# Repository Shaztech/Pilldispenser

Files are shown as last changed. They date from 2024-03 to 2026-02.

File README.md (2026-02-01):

# Automatic Pill Dispenser

Complete open source project with cheap and easily available parts (listing below).
All 3d printable parts are in STL format (go to makerworld for the 3D Models), Gerber PCB are packed in zip for easy drag-drop in 
your prefered provider (JCLPCB, PCBWay, etc).
Software are available in pre-compiled (bin files) for the ESP32, or all Arduino files are there so you can 
edit them. I've included all the library I used. The full LCD interface is in Squareline Studio.
Just follow the guides in order to assemble it once you have all the parts.

Please check the user manual for the usage of the device.

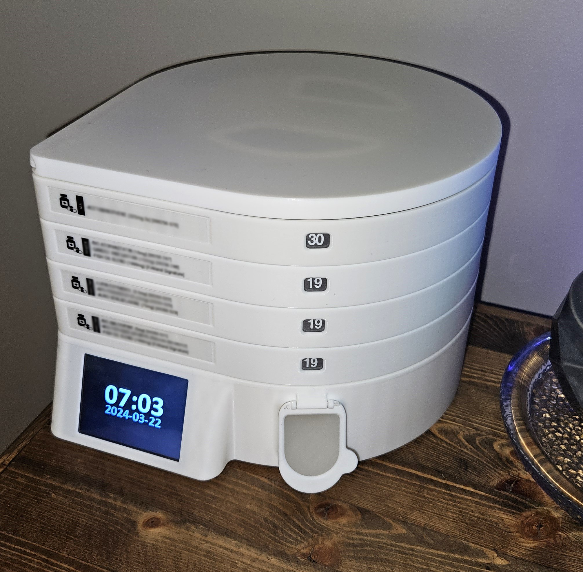
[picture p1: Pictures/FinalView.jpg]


## Features:
- USB Powered (5V, 500mah)
- Wifi configuration directly on the screen
- NPT automaticaly updated time (Need Wifi for the time to work)
- UTC/DST configurable on the screen
- Time/Date screensaver (can be disabled)
- Full interface on the touch screen
- Multiples users can be defined by colors
- Audio/Visual Alarms for each tray/users (audio alarms are repeated every minute till dispensed)
- Alarms are mp3 files on the SD card (so can be changed by the user)
- Can stack up to 10 trays
- 30 sections (can accomodate multiple/large pills) for each tray
- Manual dispense of each tray
- Visual indication of remaining pills (P-Touch label 30 to E)
- Web interface for easy configuration with browser
- Telegram integration
- [Home Assistant Integration](https://github.com/demrios-de/Pill-Dispenser-Integration-for-Home-Assistant) [EN/DE] (made by [demrios](https://github.com/demrios-de))

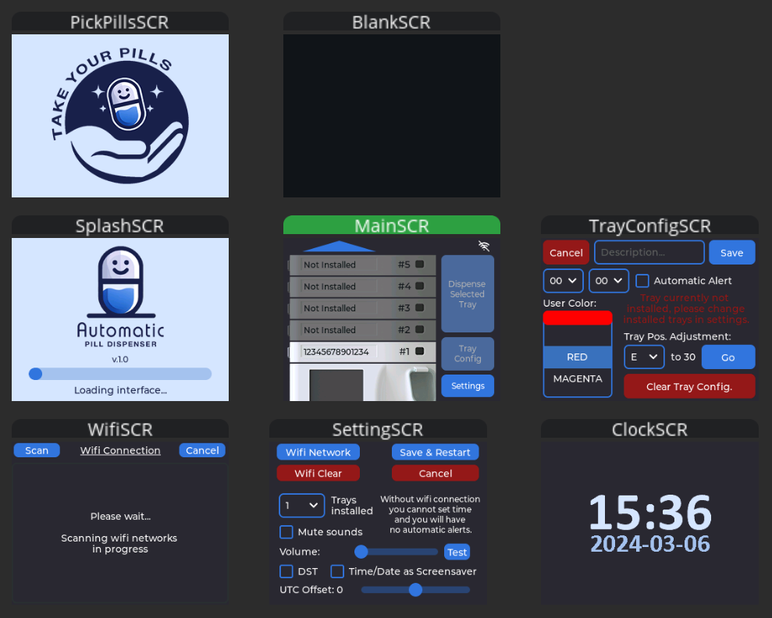
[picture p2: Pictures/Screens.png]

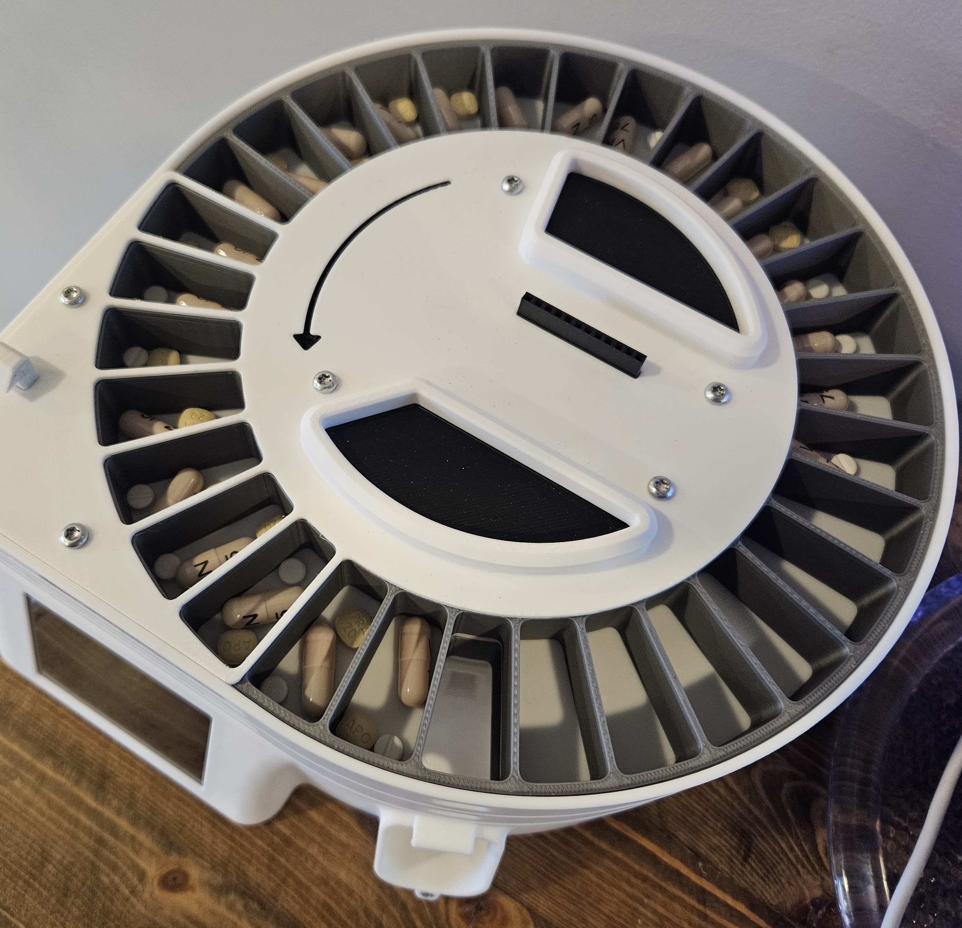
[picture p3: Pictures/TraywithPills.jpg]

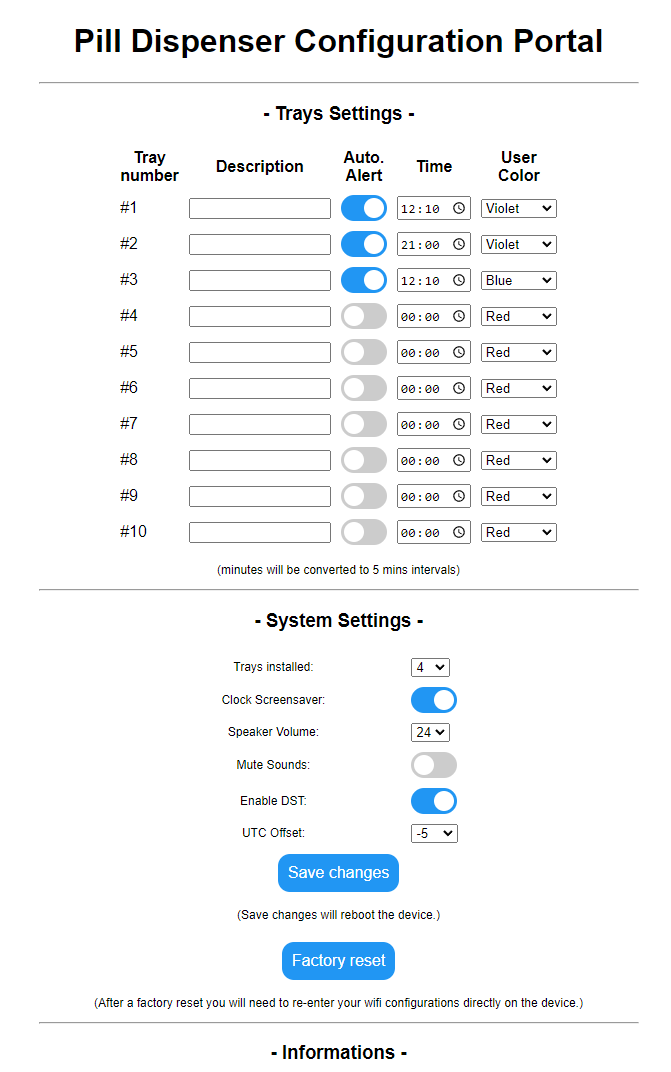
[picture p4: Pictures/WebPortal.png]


## Part listing:
(A## = Printed parts, B# = PCB, B#.# = PCB Parts, P# = Parts purchased, S# = Screws)

### Printed parts [(complete profile in makerworld)](https://makerworld.com/en/models/389626):

- A1 - Base Bottom [1x] (Printed with supports for the top of the lcd, the usb port and the base of the dispenser opening, 15% infill)
    - There's 2 base version, one with a chute and a door, the other one is with a removable cup
- A1.1 - Base Washer Holder [3x optional] (no supports, 15% infill)
- A1.2 - Cup (for the base A1b ONLY) [1x]
- A2 - LCD Holder [1x] (buildplate supports, 50% infill)
- A3 - DFPlayer Shim [1x]
- A4 - Base Top [1x].stl
- A5 - Lock Clip [1x Base + 1x per Tray]
- A6 - Base Dispense Door (for the A1 base only) [1x]
- A7 - Tray Base [1x per Tray]
- A8 - Finger [1x per Tray]
- A9 - Arm Cap [1x per Tray]
- A10 - Arm Lock [1x per Tray]
- A11 - Arm [1x per Tray]
- A12 - SG90 Cam [1x per Tray]
- A13 - CW Rotation Lock [1x per Tray]
- A14 - Tray Top [1x per Tray]
- A15 - Rotating Tray [1x per Tray]
- A16 - Tray Lock [1x per Tray]
- A17 - Top Dust Cap [1x]

### PCB parts:
- B1 - Base PCB [1x]
  - B1.1 - PCA9685 IC (TSSOP28) [1x]
  - B1.2 - SMD Capacitor 1000uf/10V (Ø10mm) [1x]
  - B1.3 - SMD Capacitor 10uf/6.3V (1206) [1x]
  - B1.4 - SMD Resistors 10Kohm (1206) [2x]
  - B1.5 - SMD Resistors 220ohm (1206) [10x]
  - B1.6 - PCB Header 12 pins Female [1x]
- B2 - LED WS2812B PCB [1x]
  - B2.1 - WS2812B 5050 LED [1x]
  - B2.2 - SMD Capacitor 0.1uf/6.3V (1206) [1x]
  - B2.3 - 74AHCT125D (SOIC14) [1x]
- B3 - Tray PCB [1x per tray]
  - There's now 2 version of the board (Straight and shifting). The shifting version (original),
  is for trays that always will be in stacking order (trays 1 at the bottom and 10 at the top).
  The straight version, is to designate a certain tray to be #1 or 2... and can be placed anywhere in the stack.
  ONLY USE ONE MODEL OF THE PCB - DO NOT MIX.
  - B3.1 - PCB Header 12 pins Male [1x per tray]
  - B3.2 - PCB Header 12 pins Female [1x per tray]
 
### Parts purchased:
- P1 - ESP-32 (ESP32-2432S028) WROOM Development Board with LCD 320x240, resistive touch, 2.8 inch (Called CYD "Cheap Yellow Display")  [1x]
- P2 - Ø30mm 2W Speaker (or anything that fit in the case) [1x]
- P3 - USB-C Female connector PCB (I used the 4 pins blue ones but any model that fit in the hole) [1x]
- P4 - DFPlayer Mini board [1x]
- P5 - MicroSD Card (smallest/cheapest you can find, only needed for 2 tiny MP3) [1x]
- P6 - Ø5mm x 1.5mm Neodinum magnet [1x]
- P7 - Ø12mm rubber or foam pads [5x]
- P8 - SG90 Servo 180° PWM Analog (Blue type is fine) [1x per tray]
- P9 - Ball pen springs (0.4x4.5x18mm) [3x per tray]
- P10 - Ø1.5mm x 14mm rod (I used Aluminium TIG rod, you can use anything that fit) [1x per tray]
- P11 - Ø1.5mm x 12mm rod (I used Aluminium TIG rod, you can use anything that fit) [1x per tray]
- P12 - Torsion Spring - McMaster #9271K71 [1x per tray]
- P-Touch Label 12mm
- S1 - Torx Screws #2 x 3/8" - McMaster #99512A159 [8x Base, 10x per tray]
- S2 - Torx Screws #4 x 1/2" - McMaster #99512A219 [8x Base, 6x per tray]

## Assembly/Notes:

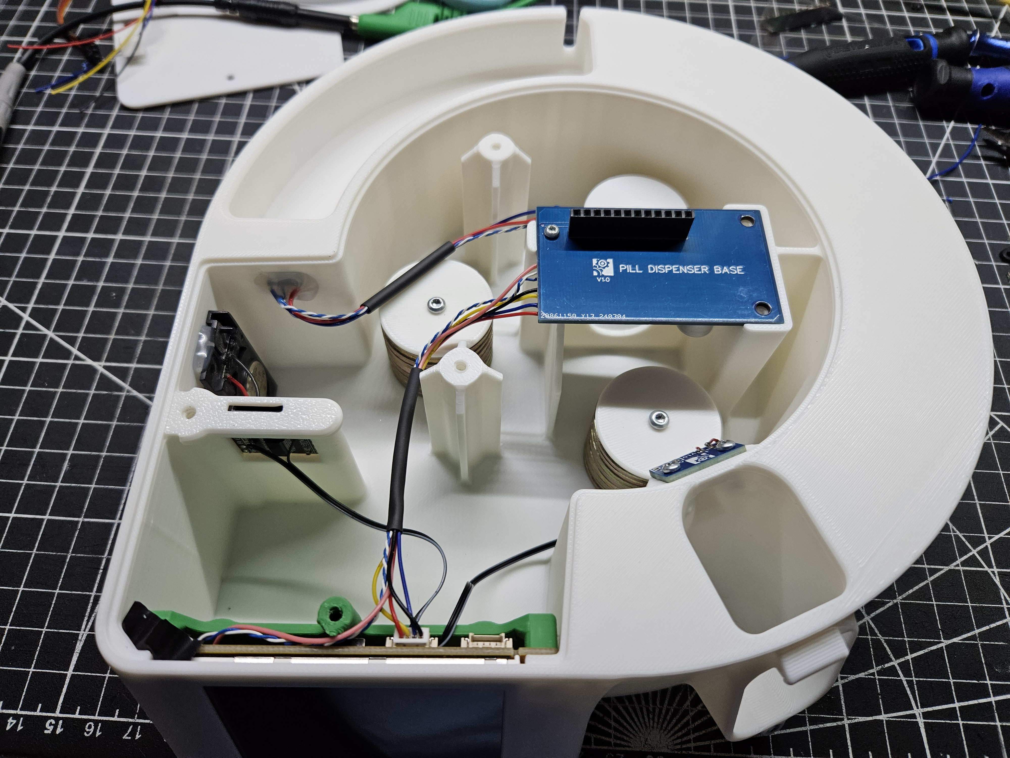
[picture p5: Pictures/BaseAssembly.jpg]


### Note #1:
Fill the hole with hot glue after you carefully placed and aligned the usb connector.
You can hold it in place with a USB-C cable plugged in the other end.

### Note #2:
You can add 24 flat washers Ø5/8" and print the A1.1 washers holders, to add weight to the base.

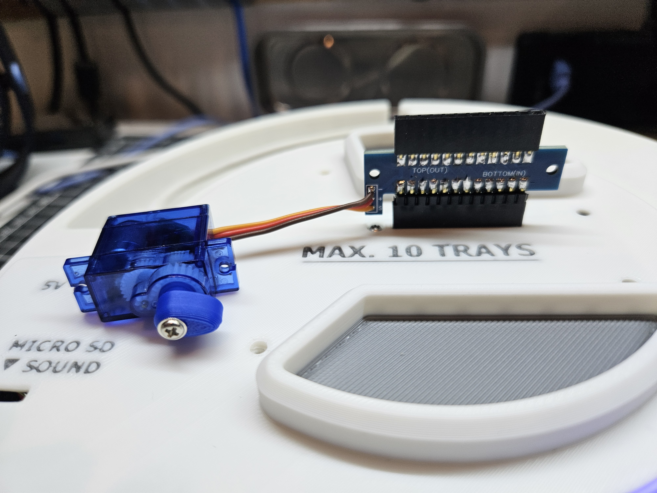
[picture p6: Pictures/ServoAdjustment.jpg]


### Note #3:
Before you install the A12 Cam to the servo, connect the PCB with the servo into the base. And power the base. 
The servo will self align to the resting position and install the cam like in the picture.

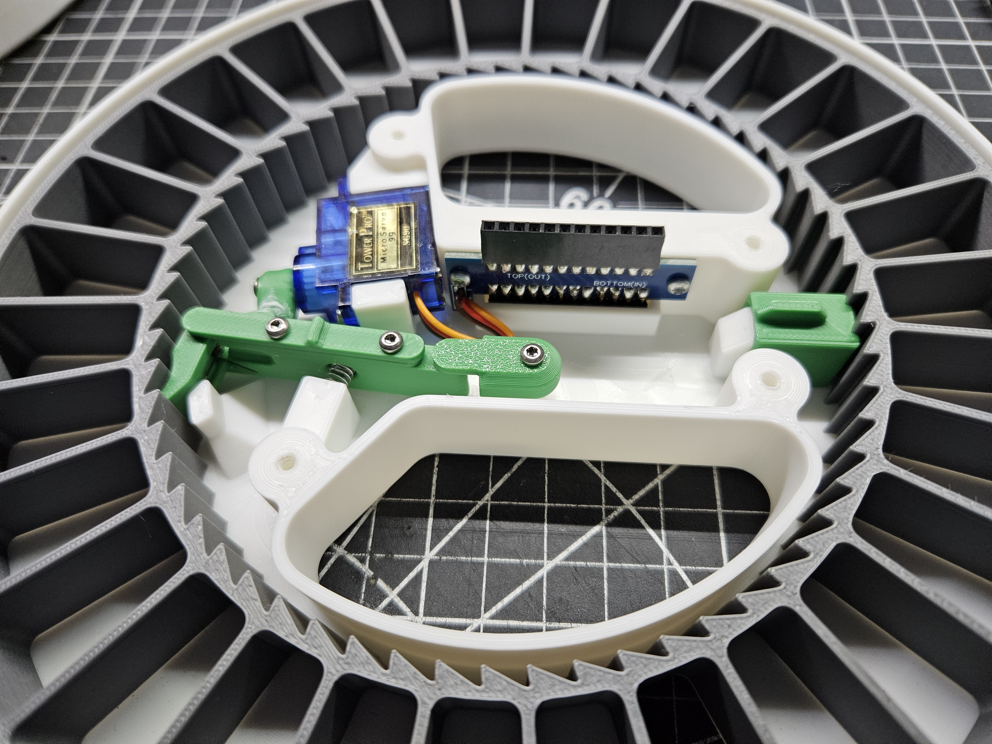
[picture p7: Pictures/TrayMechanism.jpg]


Arm V2:

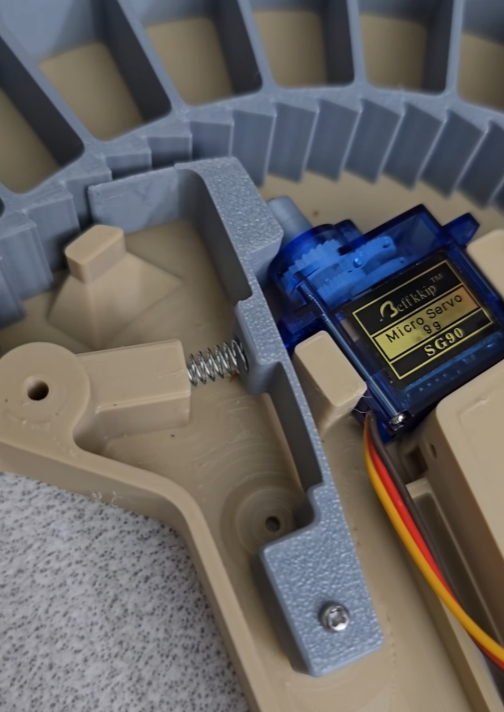
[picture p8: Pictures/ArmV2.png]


### Note #4:
There's a notch and a line printed in the rotating tray (A15), so you can align 
the P-Touch label from the start of the label all around the ring (starting with E, ending with 30).

### Note #5:
When you insert the ring be sure that the hole in the bottom of 
the tray is fully align with a container in the ring. (Not half of 2 containers)

### Note #6:
The top dust cap have a hole to insert the stylus that usually come with the LCD module when you buy it.

## Firmware flashing:
### The first Firmware Installation:
- Download the 5 bin files in this release
- Download the esptool.exe from here https://github.com/espressif/esptool/releases/tag/v4.7.0
- Copy the 5 bin files to the root of the folder (with esptool.exe)
- Connect your device (the ESP32 module with the LCD) to your computer via USB
- Find the Serial COM port number (in device manager)
- open a command line inside your folder and type, change the COM port that match your device (don't forget to change the files version ex: v1.3):

esptool.exe --chip esp32 --port COM4 --baud 921600 --before default_reset --after hard_reset write_flash -z --flash_mode dio --flash_freq 80m --flash_size 4MB 0x1000 PillDispenser.bootloader.v1_3.bin 0x8000 PillDispenser.partitions.v1_3.bin 0xe000 boot_app0.bin 0x10000 PillDispenser.esp32.v1_3.bin 0x3D0000 PillDispenser.spiffs.v1_3.bin

### In the future if there's an update:
Use the OTA update page in the web portal of the device, only 2 bin files are needed (esp32 and spiff)

## Buying parts kit (and assembled electronic):
[jsondag](https://github.com/jsondag) is selling kits, you can email him at: 09-snakes.timbres@icloud.com for more informations.

Here is his list of price as of 2025-01-04
<p style="margin: 0.0px 0.0px 0.0px 0.0px; font: 12.0px Helvetica; min-height: 13.8px"><span style="font-family: 'Helvetica'; font-weight: normal; font-style: normal; font-size: 12.00px"></span><br></p>

Description | Quantity | Unit Price | Cost
-- | -- | -- | --
Main PCB, with components, smd assembly, loose pin header | 1 | $16.00 | $16.00
USB socket | 1 | $2.00 | $2.00
LED PCB, with components, smd assembly, loose pin header | 1 | $10.00 | $10.00
Tray PCB, with loose pin headers, straight through. | 10 | $1.00 | $10.00
ESP32 2.8” CYD display dev board. | 1 | $14.00 | $14.00
30mm 2W 8ohm Speaker | 1 | $2.00 | $2.00
DFPlayer mini | 1 | $3.00 | $3.00
Servo  SG90 (buy 1 per tray) | 10 | $2.50 | $25.00
P-Touch Number labels, White on Clear (buy 1 per tray) | 10 | $1.00 | $10.00
3mm OD left hand torsion spring (buy 1 per tray) | 10 | $1.50 | $15.00
Ballpoint pen springs x3 (buy 1 per tray) | 10 | $0.50 | $5.00
Tray Screws #2x5/16” (X10) #4x1/2” (x6). (buy 1 per tray) | 10 | $1.50 | $15.00
Base Screws #2x5/16” (X8) #4x1/2” (x8) | 1 | $1.50 | $1.50
Tig Rod (hinges) | 1 | $1.00 | $1.00
128MB micro SD card | 1 | $3.00 | $3.00
  |   |   |  
  |   |   |  
  |   |   |  
  |   | Subtotal | $132.50
  |   | US Shipping | $8.00
  |   | Total | $140.50
<p style="margin: 0.0px 0.0px 0.0px 0.0px; font: 12.0px Helvetica; min-height: 13.8px"><span style="font-family: 'Helvetica'; font-weight: normal; font-style: normal; font-size: 12.00px"></span><br></p>
<br class="Apple-interchange-newline">

## [Buy me a coffee](https://www.buymeacoffee.com/shaztech_info).

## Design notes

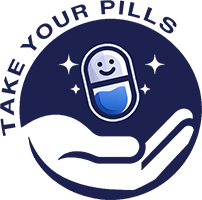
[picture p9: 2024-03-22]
Squareline Studio/assets/APD_Takepills.png

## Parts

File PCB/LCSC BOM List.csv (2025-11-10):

Index | LCSC# | MPN | Manufacturer | Package | Customer # | Description | RoHS | Quantity | MOQ | Multiple | Unit Price($) | Extended Price($) | Product Link
1 | C2678753 | PCA9685PW,118 | NXP | TSSOP-28 |  | 100kHz~1MHz PWM 16 25mA 2.3V~5.5V TSSOP-28 LED Drivers ICs RoHS | yes | 1 | 1 | 1 | 3.1136 | 3.11 | https://www.lcsc.com/product-detail/C2678753.html
2 | C99833 | RVT1A102M0810 | ROQANG | SMD,D8xL10.2mm |  | 1000uF 10V ±20% 270mA@120Hz SMD,D8xL10.2mm Aluminum Electrolytic Capacitors RoHS | yes | 10 | 10 | 10 | 0.0520 | 0.52 | https://www.lcsc.com/product-detail/C99833.html
3 | C9807 | CL31A106KAHNNNE | Samsung Electro-Mechanics | 1206 |  | 25V 10uF X5R ±10% 1206 Ceramic Capacitors RoHS | yes | 10 | 10 | 10 | 0.0209 | 0.21 | https://www.lcsc.com/product-detail/C9807.html
4 | C17902 | 1206W4F1002T5E | UNI-ROYAL | 1206 |  | 10kΩ 250mW 200V ±100ppm/℃ Thick Film Resistor ±1% 1206 Chip Resistor - Surface Mount RoHS | yes | 100 | 100 | 100 | 0.0031 | 0.31 | https://www.lcsc.com/product-detail/C17902.html
5 | C2933785 | FRC1206J221 TS | FOJAN | 1206 |  | 250mW 220Ω 200V ±100ppm/℃ Thick Film Resistor ±5% 1206 Chip Resistor - Surface Mount RoHS | yes | 100 | 100 | 100 | 0.0019 | 0.19 | https://www.lcsc.com/product-detail/C2933785.html
6 | C114586 | WS2812B-B/W | Worldsemi | SMD5050-4P |  | SMD5050-4P LED Addressable, Specialty RoHS | yes | 5 | 5 | 5 | 0.0837 | 0.42 | https://www.lcsc.com/product-detail/C114586.html
7 | C24497 | CL31B104KBCNNNC | Samsung Electro-Mechanics | 1206 |  | 50V 100nF X7R ±10% 1206 Ceramic Capacitors RoHS | yes | 20 | 20 | 20 | 0.0138 | 0.28 | https://www.lcsc.com/product-detail/C24497.html
8 | C2840012 | PZ254V-11-12P | XFCN | Through Hole,P=2.54mm |  | 12P 1x12P -40℃~+105℃ Black Pin Header 2.54mm 2.5mm 6mm 250V 3mm 1 3A Through Hole Through Hole,P=2.54mm Headers, Male Pins RoHS | yes | 10 | 10 | 10 | 0.0687 | 0.69 | https://www.lcsc.com/product-detail/C2840012.html
9 | C2905419 | KH-2.54FH-1X12P-H8.5 | kinghelm | Through Hole,P=2.54mm |  | 2.54mm 1 12P -40℃~+105℃ 1x12P 8.5mm Top 3A Square Hole Through Hole Through Hole,P=2.54mm Headers, Receptacles, Female Sockets RoHS | yes | 15 | 5 | 5 | 0.1169 | 1.75 | https://www.lcsc.com/product-detail/C2905419.html
10 | C5962 | 74HCT125D,653 | Nexperia | SOIC-14 |  | 1 160uA 4.5V~5.5V 4 15ns@4.5V,50pF SOIC-14 Buffers, Drivers, Receivers, Transceivers RoHS | yes | 5 | 5 | 5 | 0.2284 | 1.14 | https://www.lcsc.com/product-detail/C5962.html

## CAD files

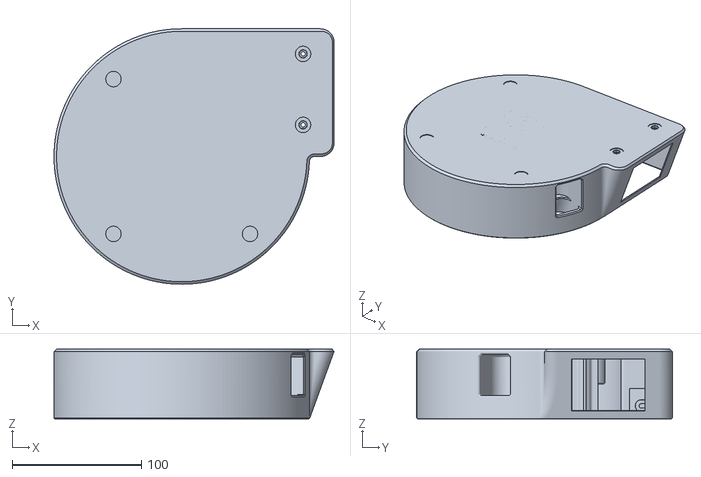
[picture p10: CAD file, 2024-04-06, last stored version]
3D Printed Parts STL/A1b - Base Bottom - Model with cup [1x].stl
217.0 x 198.0 x 54.0

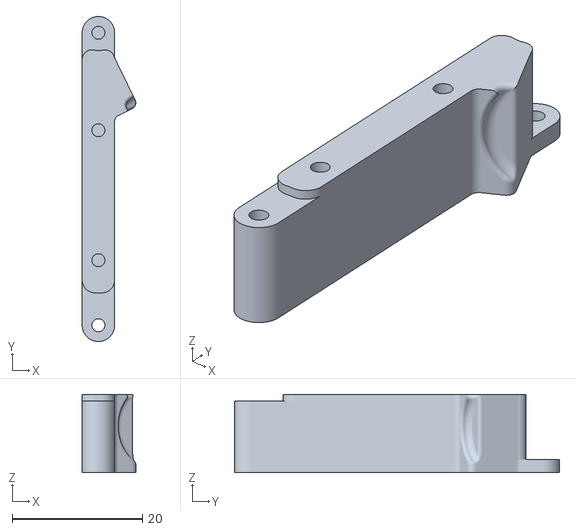
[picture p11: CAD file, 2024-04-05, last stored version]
3D Printed Parts STL/A11 - Arm [1x per Tray].stl
8.26 x 50.0 x 12.0

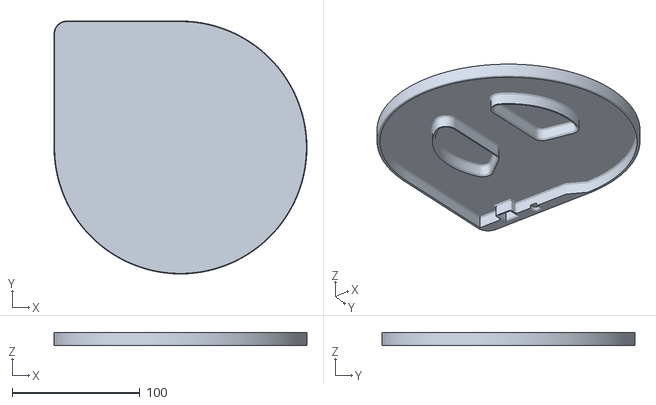
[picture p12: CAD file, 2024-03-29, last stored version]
3D Printed Parts STL/A17 - Top Dust Cap [1x].stl
198.0 x 198.0 x 10.5

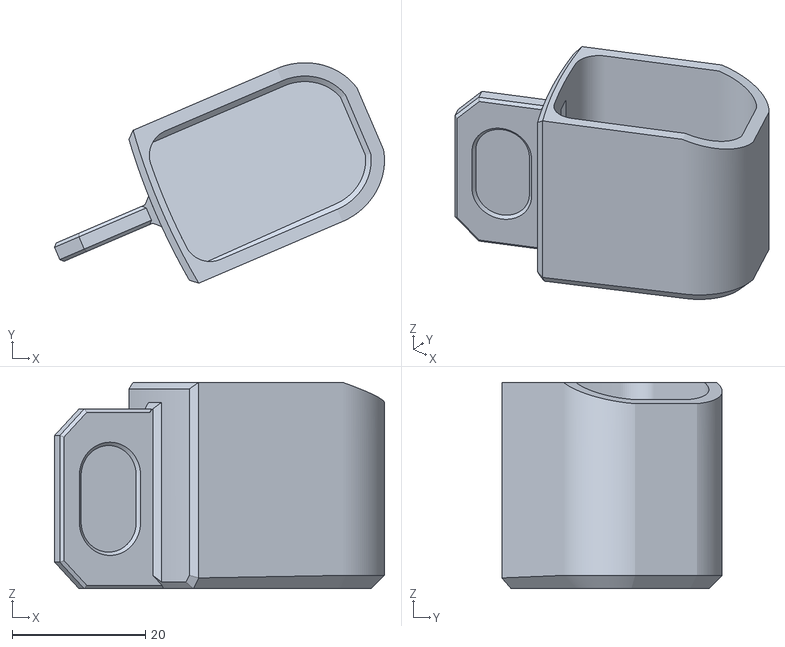
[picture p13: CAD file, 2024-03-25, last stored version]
3D Printed Parts STL/A1.2 - Base Cup [1x OPT].stl
49.6 x 33.1 x 31.0

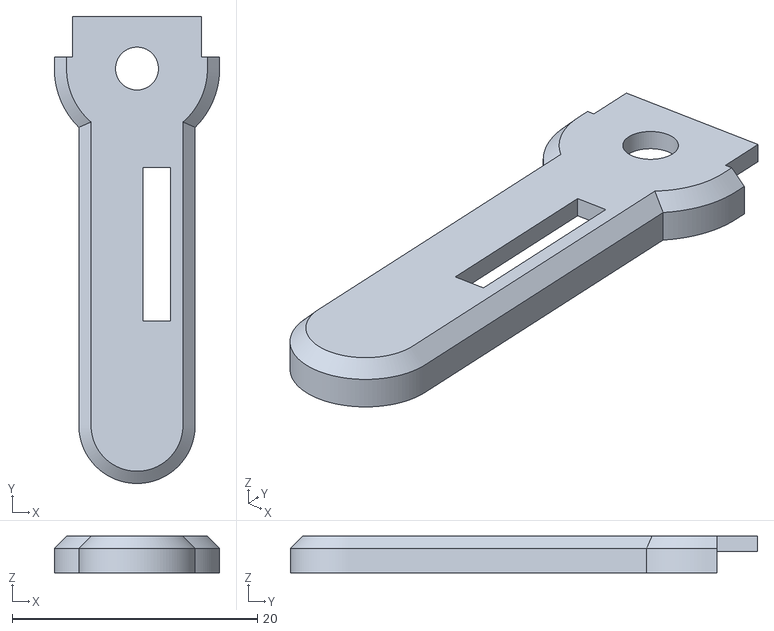
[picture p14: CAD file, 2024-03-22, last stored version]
3D Printed Parts STL/A3 - DFPlayer Shim [1x].stl
13.5 x 38.1 x 3.00

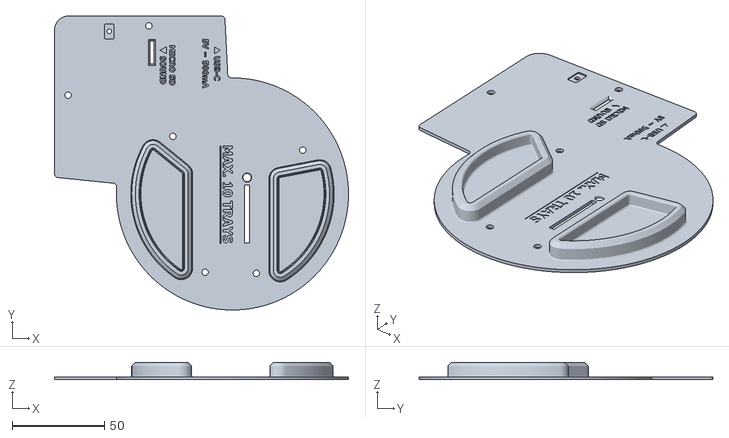
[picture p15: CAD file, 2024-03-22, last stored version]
3D Printed Parts STL/A4 - Base Top [1x].stl
159.6 x 159.6 x 9.50

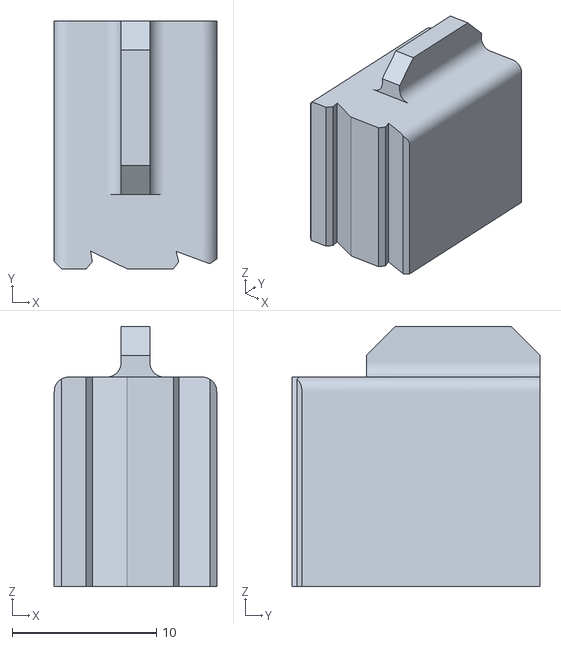
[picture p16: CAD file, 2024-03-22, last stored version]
3D Printed Parts STL/A13 - CW Rotation Lock [1x per Tray].stl
11.2 x 17.2 x 18.0

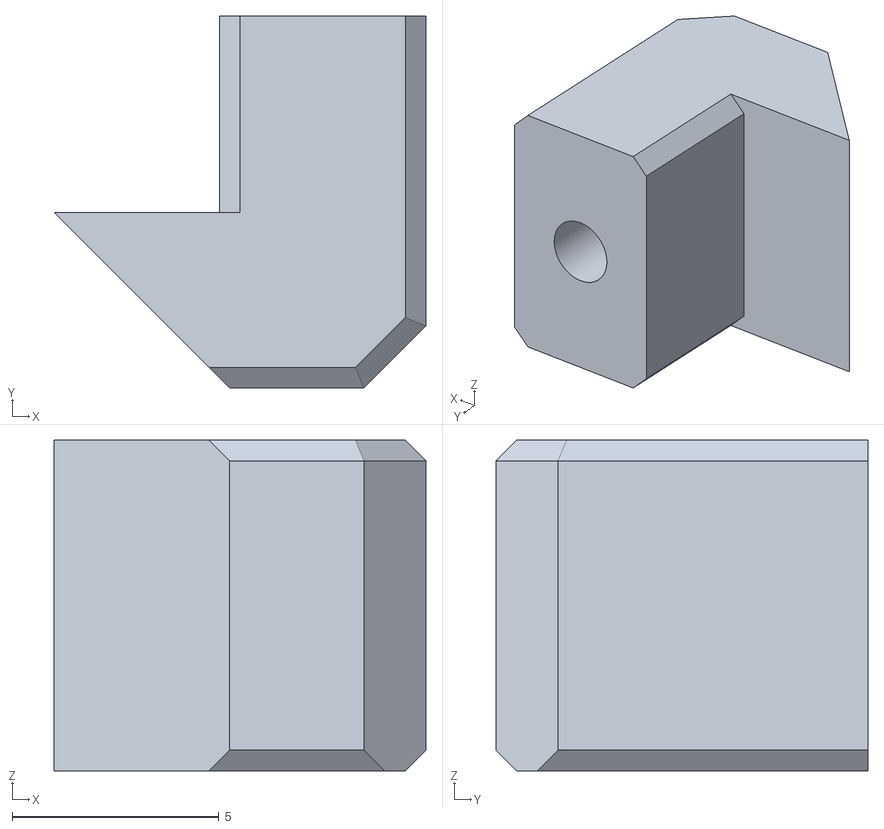
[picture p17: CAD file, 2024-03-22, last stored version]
3D Printed Parts STL/A5 - Lock Clip [1x Base + 1x per Tray].stl
9.00 x 9.00 x 8.00

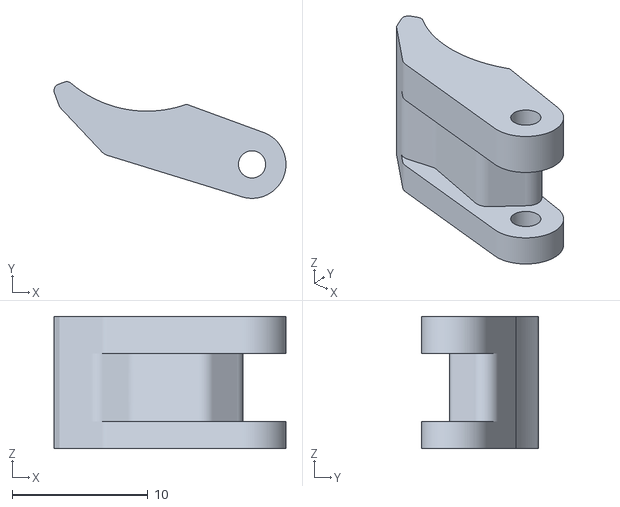
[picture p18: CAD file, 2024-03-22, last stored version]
3D Printed Parts STL/A8 - Finger [1x per Tray].stl
17.1 x 8.59 x 9.75

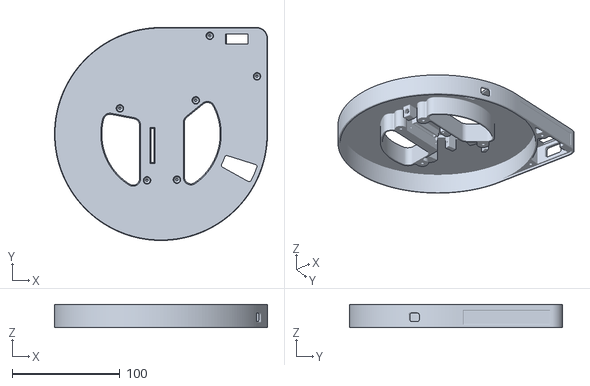
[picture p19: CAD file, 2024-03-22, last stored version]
3D Printed Parts STL/A7 - Tray Base [1x per Tray].stl
198.0 x 198.0 x 21.5

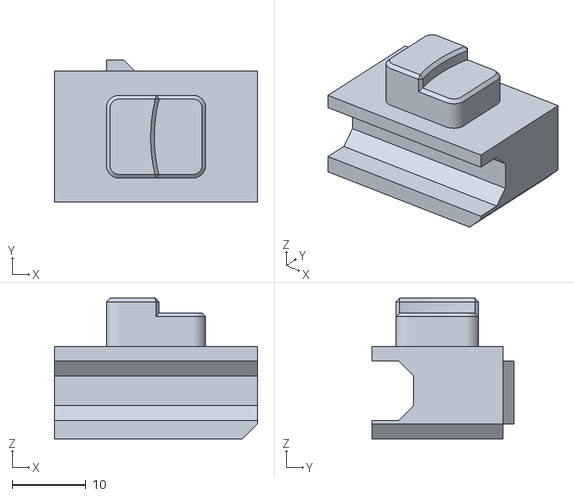
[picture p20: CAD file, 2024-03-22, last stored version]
3D Printed Parts STL/A16 - Tray Lock [1x per Tray].stl
27.5 x 19.2 x 19.0

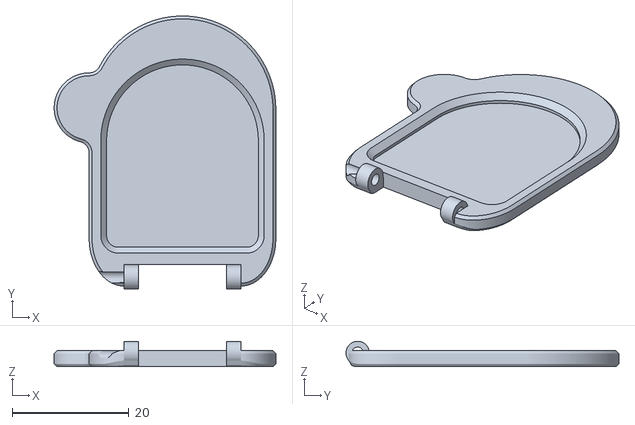
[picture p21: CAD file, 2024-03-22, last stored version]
3D Printed Parts STL/A6 - Base Dispense Door [1x].stl
38.0 x 46.8 x 4.37

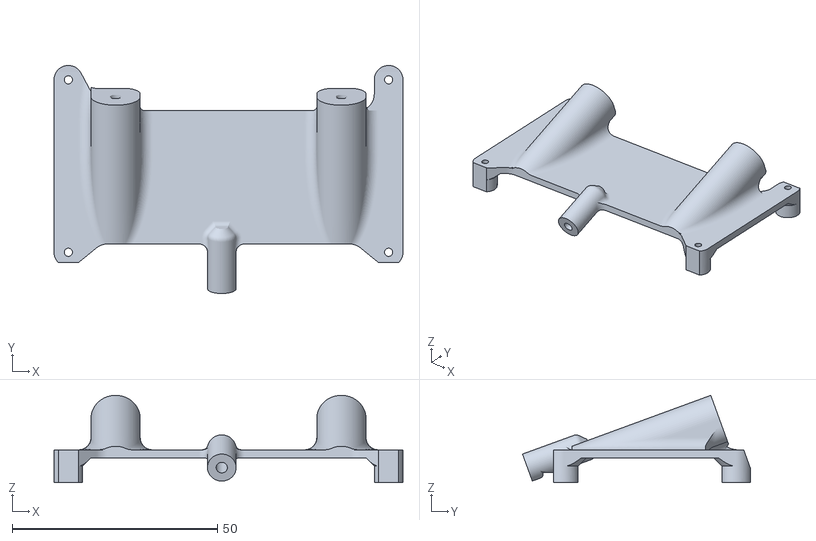
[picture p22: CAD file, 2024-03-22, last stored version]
3D Printed Parts STL/A2 - LCD Holder [1x].stl
85.0 x 55.5 x 21.3

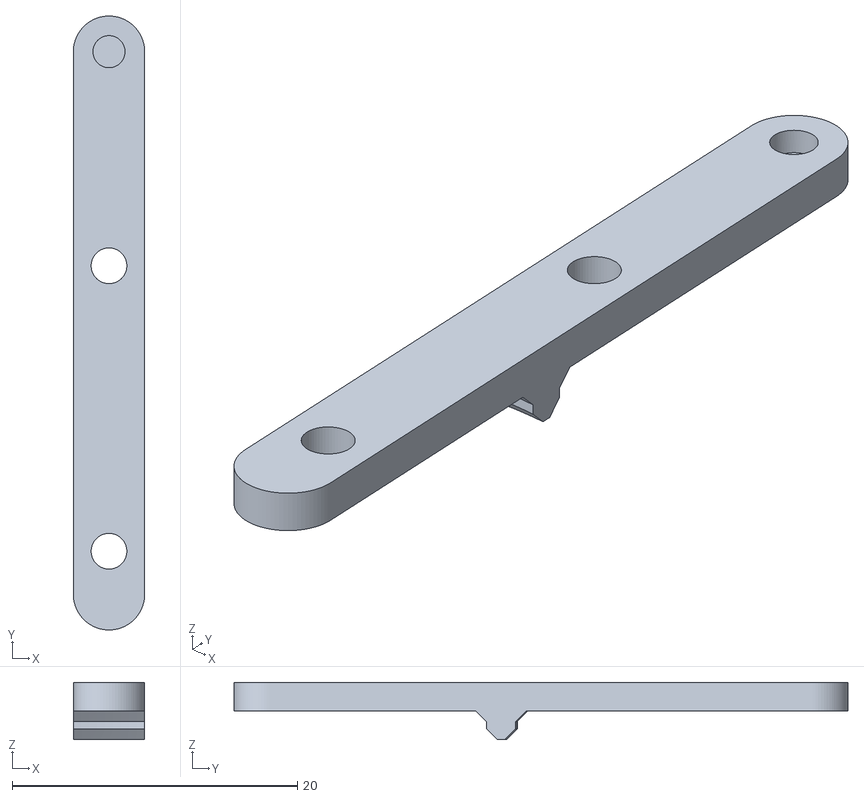
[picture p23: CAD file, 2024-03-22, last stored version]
3D Printed Parts STL/A9 - Arm Cap [1x per Tray].stl
5.00 x 43.0 x 4.00

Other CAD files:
3D Printed Parts STL/A1 - Base Bottom - Model with door [1x].stl
3D Printed Parts STL/A1 - Base Bottom - Model with cup [1x].stl
3D Printed Parts STL/A1 - Base Bottom [1x].stl
3D Printed Parts STL/A10 - Arm Lock [1x per Tray].stl
3D Printed Parts STL/A1.1 - Base Washer Holder [3x OPT].stl
3D Printed Parts STL/A12 - SG90 Cam [1x per Tray].stl
3D Printed Parts STL/A14 - Tray Top [1x per Tray].stl
3D Printed Parts STL/A15 - Rotating Tray [1x per Tray].stl

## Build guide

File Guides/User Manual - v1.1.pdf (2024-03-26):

# Automatic Pill Dispenser

# User Manual

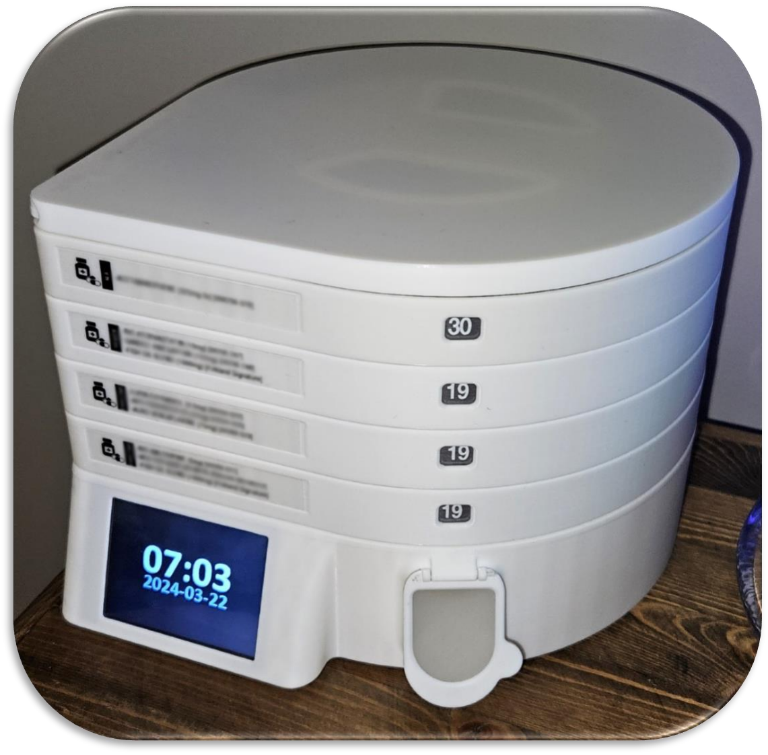
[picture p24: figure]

## for software version 1.1

A u t o m a t i c p i l l d i s p e n s e r – U s e r M a n u a l | P a g e 2 | 11

# Index

### Main screen | Page 3

### Main screen (Alerts) | Page 4

### Main screen (Checkmarks) | Page 5

### Trays configuration screen | Page 6

### Settings screen | Page 7

### Wi-Fi screen | Page 8

### Web interface | Page 9-10

### Web interface (OTA Update) | Page 11

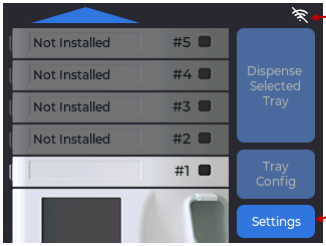
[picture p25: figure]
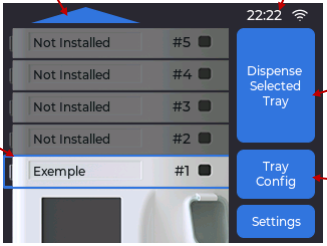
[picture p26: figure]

A u t o m a t i c p i l l d i s p e n s e r – U s e r M a n u a l | P a g e 3 | 11

# Main screen

This icon shows the Wi-Fi status

Use this button to go to the setting screen (see page 7)

When a Wi-Fi is connected you will see the time and a
connected icon (this icon doesn’t show the strength of the signal)

Use the arrow to see the upper portion of the trays (#6 to #10)

You can select any
tray by clicking on it.
(a blue border means
it’s selected)

This button dispenses the
selected tray, if this tray is configured for an alert, a checkmark will appear for
the day and the alarm will not sound.

Use this button to go to the selected tray configuration (see page 6)

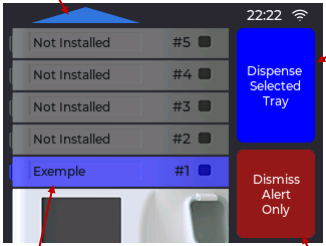
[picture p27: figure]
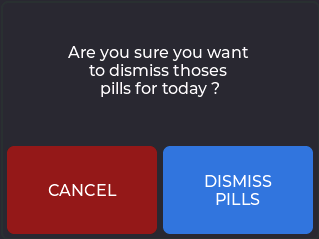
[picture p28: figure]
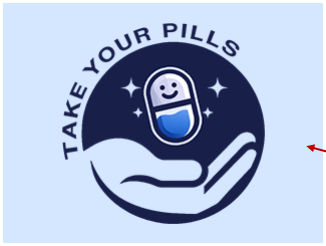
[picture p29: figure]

A u t o m a t i c p i l l d i s p e n s e r – U s e r M a n u a l | P a g e 4 | 11

# Main screen (alerts)

If an alert appends on multiple trays and some are on the upper level, this arrow will blink.

One or more tray can have an alert at the same time, the tray will blink the color selected in the configuration page.

You can dismiss an alert without dispensing the pills

This will dispense all the trays of the same color currently in alerts. The color of the button indicates the trays that will be dispensed.

When you have dispensed any trays, this screen will be displayed for 2 minutes, you can dismiss it by clicking anywhere on it.

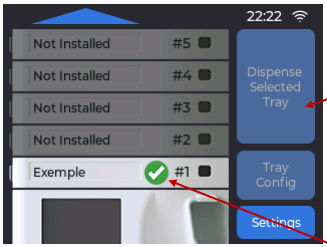
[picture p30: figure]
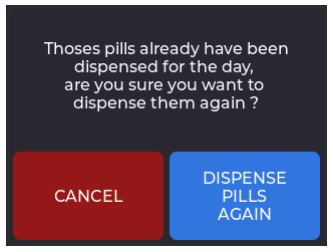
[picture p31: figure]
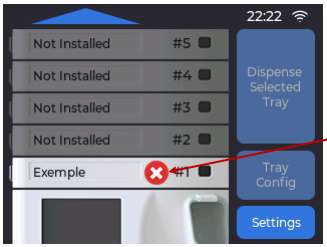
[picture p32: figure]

A u t o m a t i c p i l l d i s p e n s e r – U s e r M a n u a l | P a g e 5 | 11

# Main screen (checkmarks)

This indicate that your pills have been dispensed for the day. This will reset at the time defined in the settings (see page 7)

If you try to dispense them again this message will be shown.

This indicate that your pills have been dismissed for the day. If you dispense later the green
checkmark will appear instead.

This will reset at the time defined in the settings (see page 7)

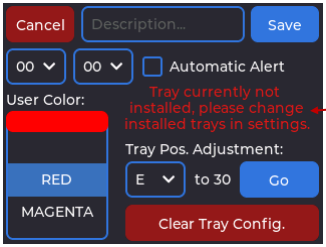
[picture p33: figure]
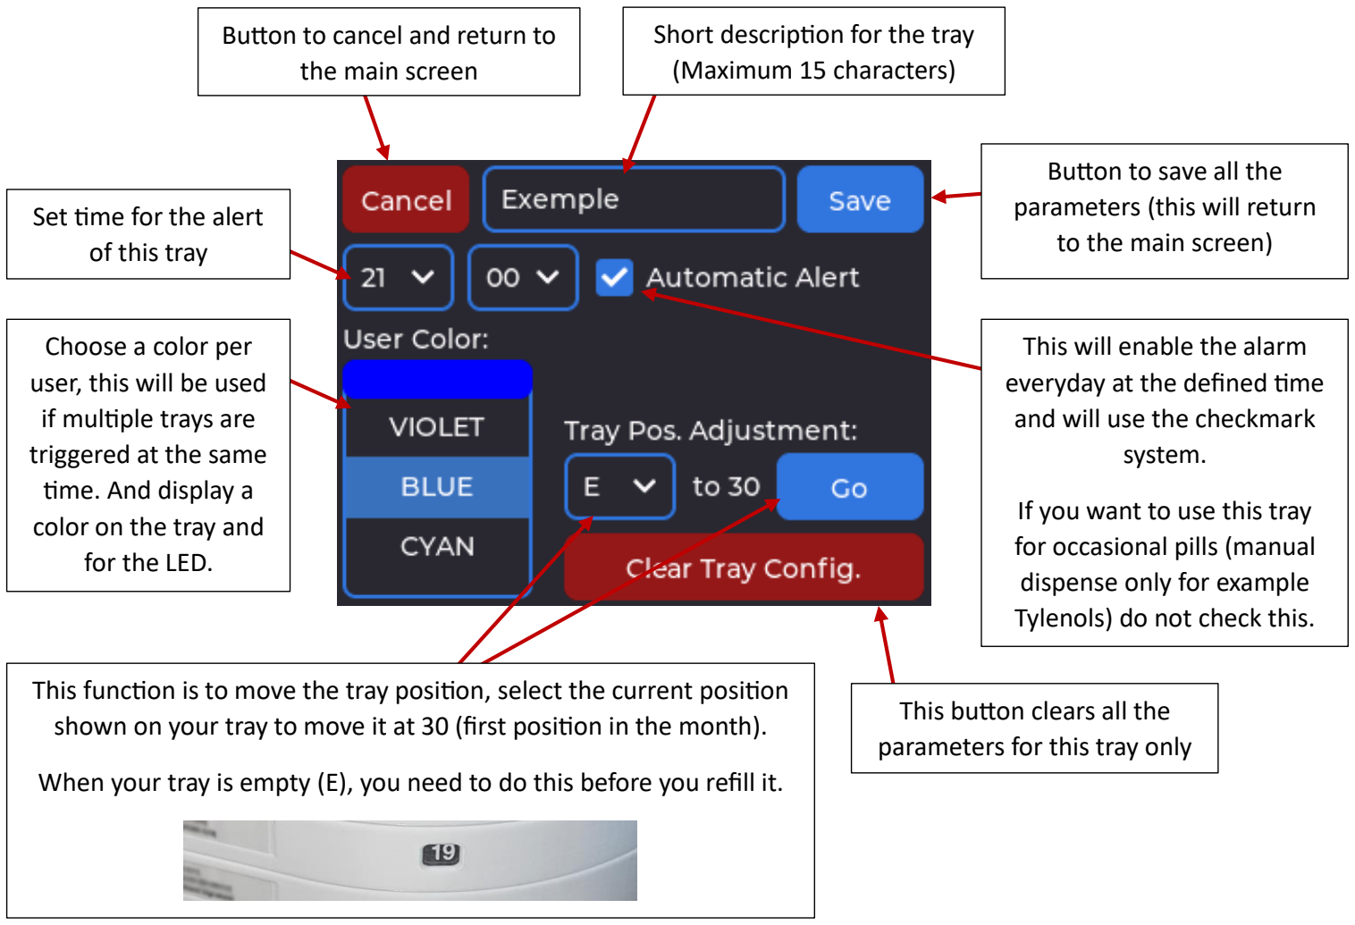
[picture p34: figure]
Button to cancel and return to the main screen; Short description for the tray (Maximum 15 characters); Button to save all the parameters (this will return to the main screen); This will enable the alarm everyday at the defined time and will use the checkmark system.; If you want to use this tray for occasional pills (manual dispense only for example Tylenols) do not check this.; This button clears all the parameters for this tray only; Set time for the alert of this tray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

A u t o m a t i c p i l l d i s p e n s e r – U s e r M a n u a l | P a g e 6 | 11

# Tray configuration screen

This message appears if your current tray is not installed. (see page 7)

But you can still configure the tray, all parameters will be saved

This function is to move the tray position, select the current position shown on your tray to move it at 30 (first position in the month).

When your tray is empty (E), you need to do this before you refill it.

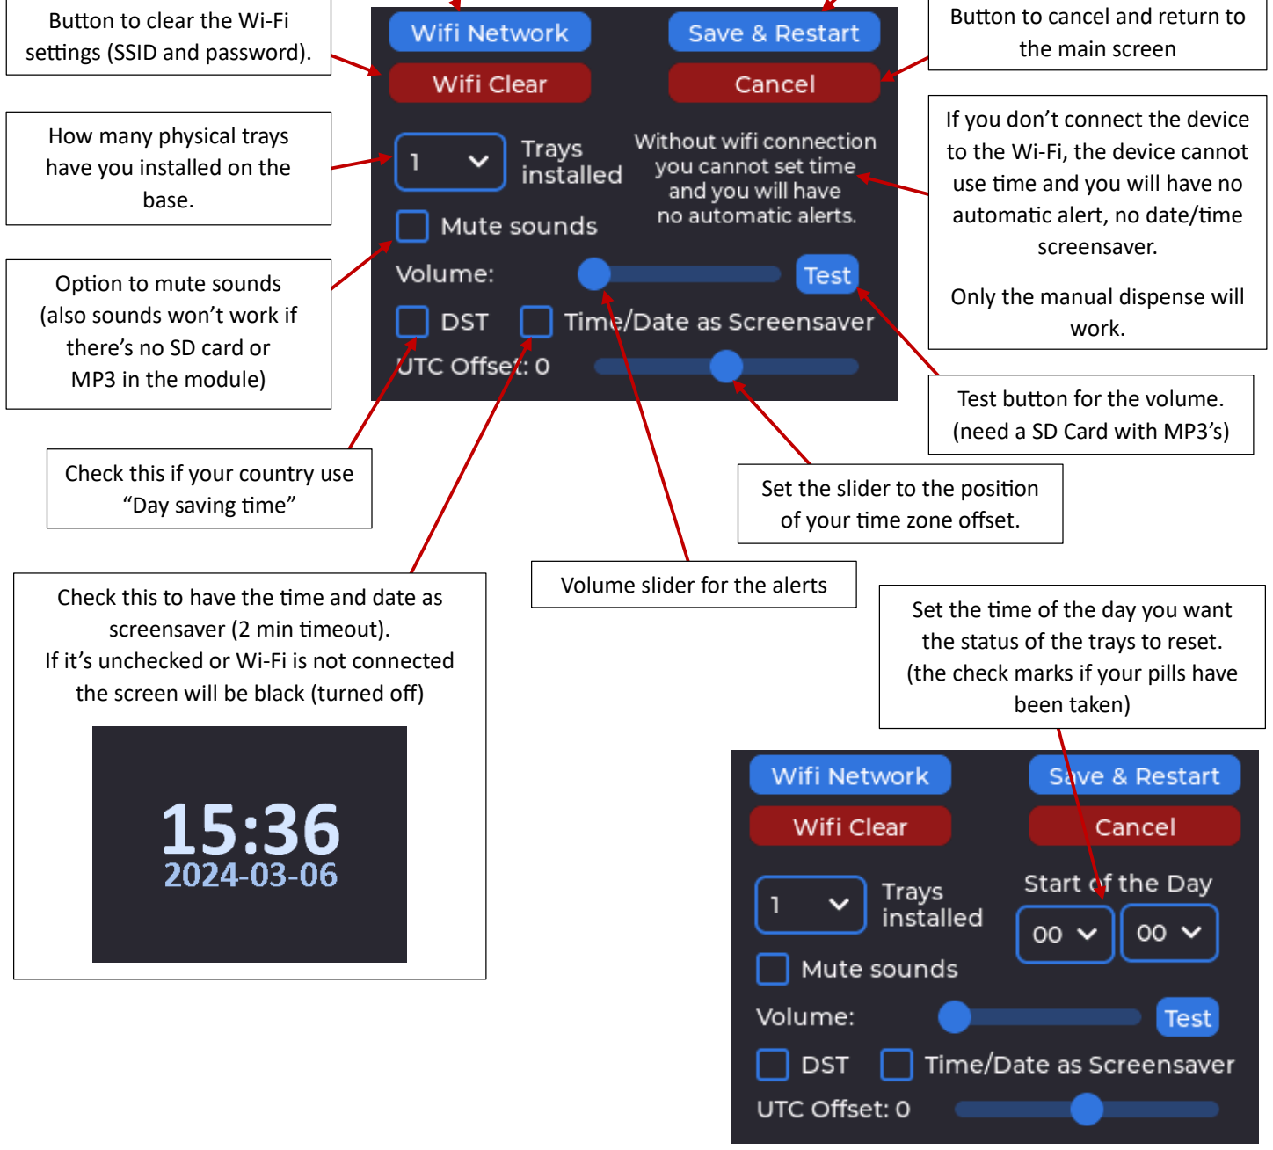
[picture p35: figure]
Set the time of the day you want the status of the trays to reset. (the check marks if your pills have been taken); Volume slider for the alerts; If you don’t connect the device to the Wi-Fi, the device cannot use time and you will have no automatic alert, no date/time screensaver.; Only the manual dispense will work.; Check this if your country use “Day saving time”; Set the slider to the position of your time zone offset.; Test button for the volume. (need a SD Card with MP3’s); Check this to have the time and date as screensaver (2 min timeout).; the screen will be black (turned off)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

A u t o m a t i c p i l l d i s p e n s e r – U s e r M a n u a l | P a g e 7 | 11

# Settings screen

If it’s unchecked or Wi-Fi is not connected

Button to go to the Wi-Fi
configuration screen
(see page 4)

Button to save all the settings (this will restart the device).

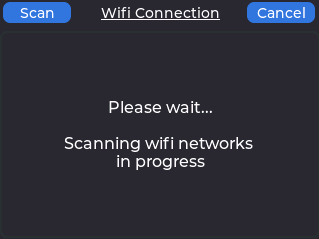
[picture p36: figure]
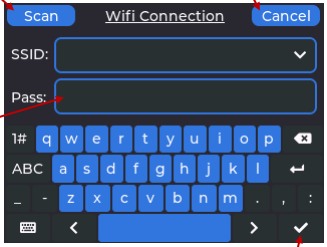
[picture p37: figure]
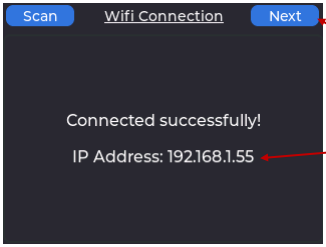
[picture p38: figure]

A u t o m a t i c p i l l d i s p e n s e r – U s e r M a n u a l | P a g e 8 | 11

# Wi-Fi screen

Use this button to scan for Wi-Fi SSID (only 2.4ghz Wi-Fi is supported) This button will return you to the setting screen (see page 3)

Enter your Wi-Fi password here

Use the checkmark to try to connect to the Wi-Fi.

When connected successfully to the Wi-Fi, you can note your IP address if you want to use the web portal (see page 10)

Use this button to return to the setting screen.

# Web interface

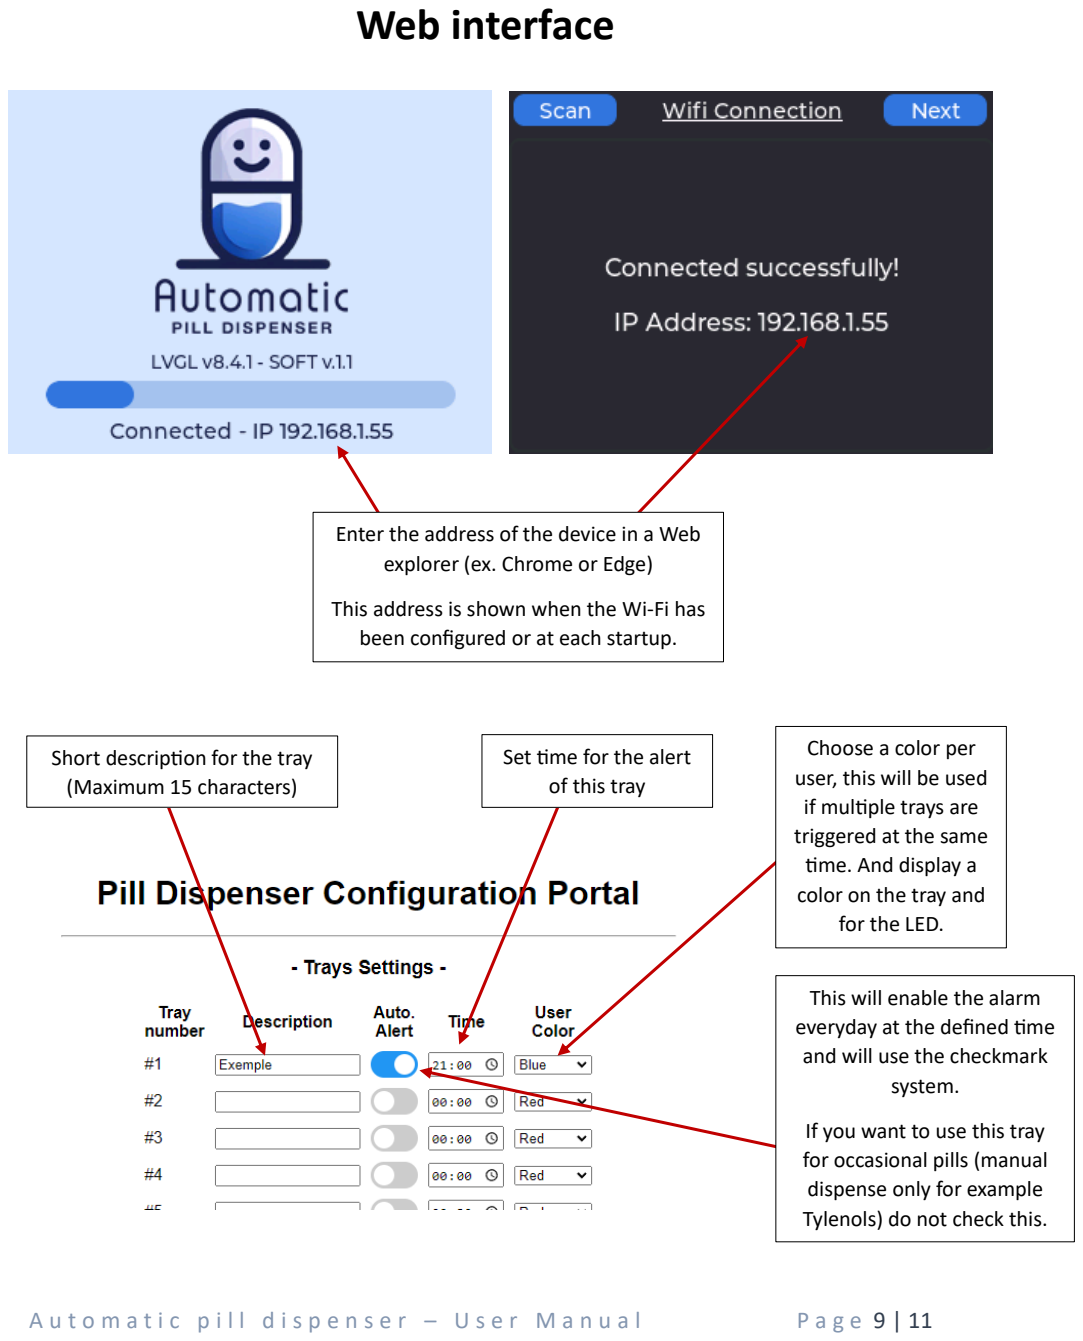
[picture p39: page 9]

A u t o m a t i c p i l l d i s p e n s e r – U s e r M a n u a l | P a g e 9 | 11

Enter the address of the device in a Web explorer (ex. Chrome or Edge)

This address is shown when the Wi-Fi has been configured or at each startup.

Short description for the tray (Maximum 15 characters)

This will enable the alarm everyday at the defined time and will use the checkmark system.

If you want to use this tray for occasional pills (manual dispense only for example
Tylenols) do not check this.

Set time for the alert
of this tray

Choose a color per
user, this will be used
if multiple trays are
triggered at the same
time. And display a
color on the tray and
for the LED.

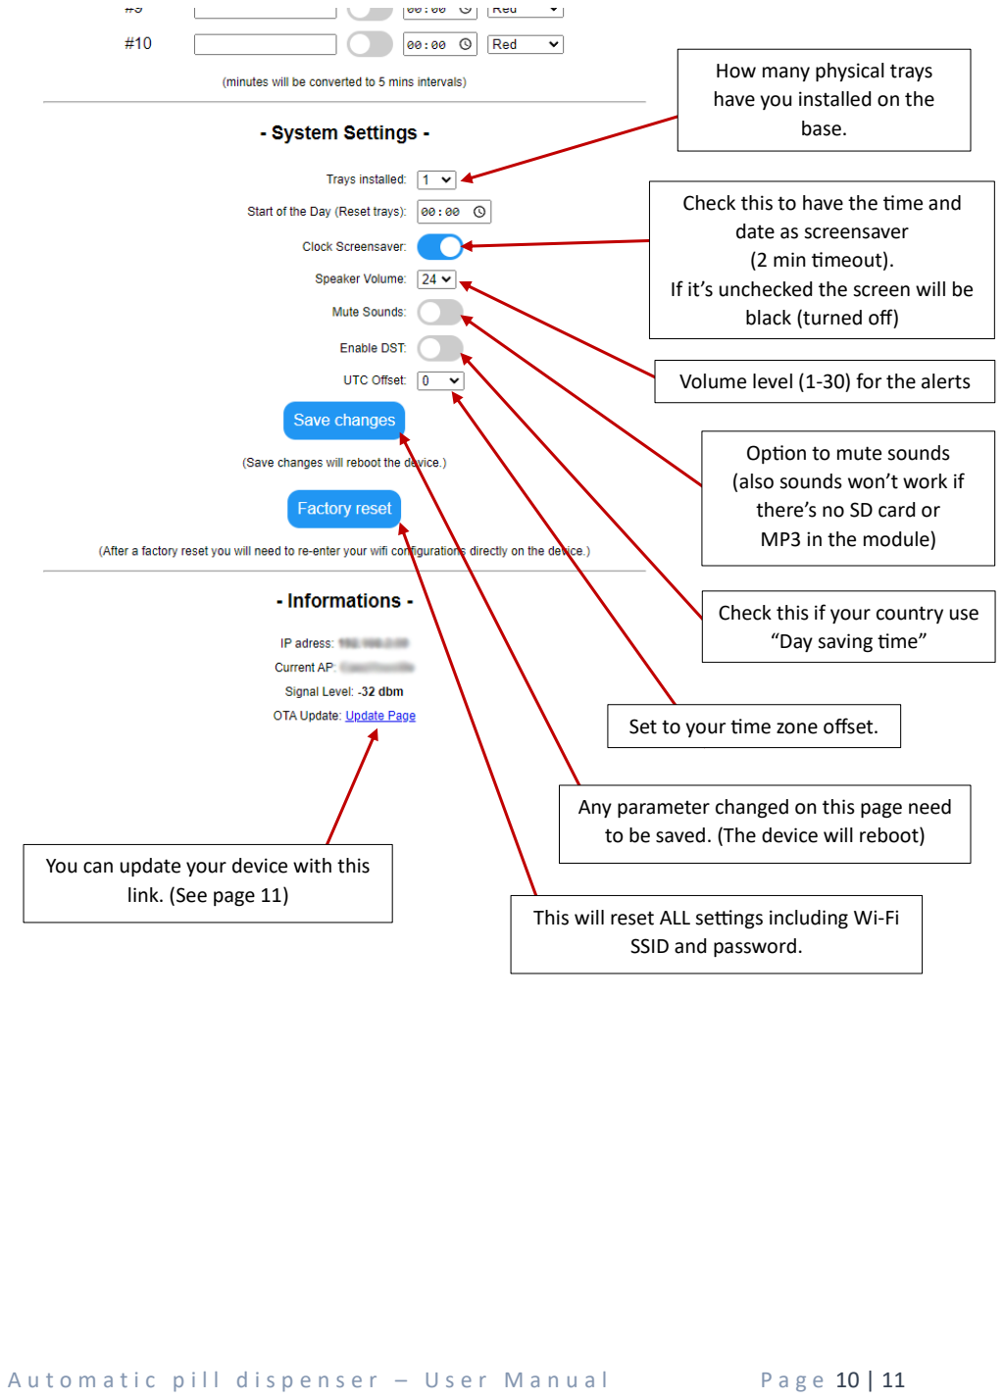
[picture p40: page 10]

A u t o m a t i c p i l l d i s p e n s e r – U s e r M a n u a l | P a g e 10 | 11

Volume level (1-30) for the alerts

Check this if your country use “Day saving time”

Check this to have the time and date as screensaver
(2 min timeout).
If it’s unchecked the screen will be black (turned off)

How many physical trays
have you installed on the
base.

Option to mute sounds
(also sounds won’t work if there’s no SD card or
MP3 in the module)

Set to your time zone offset.

Any parameter changed on this page need to be saved. (The device will reboot)

This will reset ALL settings including Wi-Fi SSID and password.

You can update your device with this link. (See page 11)

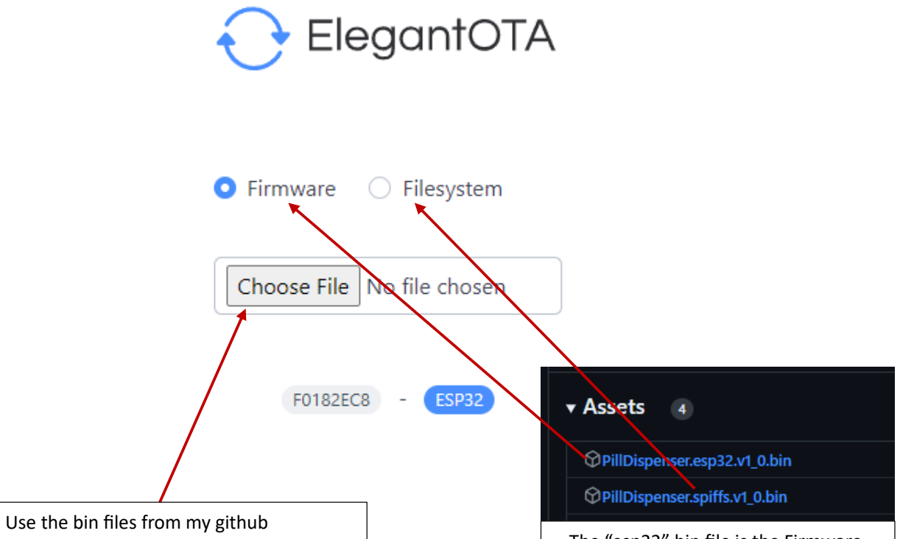
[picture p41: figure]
Use the bin files from my github

A u t o m a t i c p i l l d i s p e n s e r – U s e r M a n u a l | P a g e 11 | 11

# Web interface (update)

https://github.com/Shaztech/Pilldispenser/releases

The “esp32” bin file is the Firmware, the “spiffs” bin file is the Filesystem

Do not mix theses two.

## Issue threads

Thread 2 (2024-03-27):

### ISSUE TITLE
LCD Screen - Purchased part

### ISSUE THREAD

**Issue by tavenhall1** [Shaztech/Pilldispenser#2]
Hello, I haven't been able to find any mention of what the requirement are for the LCD screen (ie size/type/connection/etc). It's possible I missed it, so feel free to point me to that information. Can you also add it to the list of purchased parts?

Thanks!

**Comment by Shaztech** [comment]
The lcd is with the ESP32 module:
P1 - ESP-32 WROOM Development Board (Called CYD "Cheap Yellow Display") [1x]
[https://www.aliexpress.com/item/1005006604267846.html](url)
[https://www.amazon.ca/DIYmalls-ESP32-2432S028R-Resistive-ESP-WROOM-32-Development/dp/B0CG2WQGP9](url)

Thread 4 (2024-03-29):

### ISSUE TITLE
Floating parts in A17 - Top Dust Cap [1x].stl

### ISSUE THREAD

**Issue by ponymorphism** [Shaztech/Pilldispenser#4]
Hello,

first off thanks so much for your tremendous project. Very inspiring!

When printing A17 - Top Dust Cap, I noticed that the two D-shaped parts in the middle of the part seem to be floating about 0.5mm above the main surface. My slicer (OrcaSlicer) even suggested to add supports there (see screenshots).

![Screenshot 2024-03-29 074620](https://github.com/Shaztech/Pilldispenser/assets/3270981/09b2ca42-6819-4450-a627-51a40b788c38)
![Screenshot 2024-03-29 074718](https://github.com/Shaztech/Pilldispenser/assets/3270981/74794423-692a-4c8f-bac1-dda901c0e6ec)

I still tried to print it as it is (without supports), but the D-shapes didn't connect to the surface as expected. My quick fix was now to insert a flattened cube to just fill the gap.

**Comment by Shaztech** [comment]
I fixed it, when I printed mine, the overall part was lower by 1 mm, and wasn't sitting correctly on my trays, so I decided to add 1mm but never tested it. Thanks you !

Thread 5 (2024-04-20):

Shaztech/Pilldispenser #5: Green LED stays one after dispensing

jsondag, 2024-04-20:
When dispensing a tray.
If you dismiss the "Take your Pills" screen, 

at 30s, the LED comes back on green, and stays green till four minutes after dismiss. This appears to be two times the 120s screen timeout.
00:00 Dispense then dismiss.
00:30 Green LED comes on
02:00 LCD turns off.
04:00 Green LED turns off

If you don't dismiss it and let it time out.
00:00 Dispense
00:30 Take you pills goes away
02:00 Green LED comes on
04:00 Green LED turns off.

Shaztech, 2024-04-20:
Does your tray is configured for green ?

jsondag, 2024-04-21:
It’s configured for red. I’ll check the voltage when I get a moment. Seems an odd one that it happens in line with the screen timeout of 120S. It would also be nice to have a configurable timeout and a button (perhaps the image of the display on the base) that would immediately shut off the screen and LED. I was studying your code to see if I could add those things, but I’m not the best coder, so I don’t yet quite understand it.

Shaztech, 2024-04-21:
I have timers that do things in those times. And sends a command to put the LED "off" but to put an LED "off" is to send the color "0,0,0" in HEX therefore black. If there is not enough voltage the chip in the LED reacts strangely and displays green.

You want a configurable timeout/button to do what ? The LED is supposed to always be off except when there's an alert and if the screen is in "dispense". (Also a small bluish tint when it's booting)

Mine with the exact same code posted here, is working fine for over a month (multiple users and alerts per day).

Does your LED flash red (or the color of your tray) during an alert/dispense ?

jsondag, 2024-04-21:
[image]

jsondag, 2024-04-21:
A configurable timeout for the screen, and/or button to blank the screen. I tend to take my meds and then lay right down to sleep while my wife does the same. Two minutes with the screen on may annoy her.

jsondag, 2024-04-21:
https://github.com/Shaztech/Pilldispenser/assets/13071956/d11f448d-127b-478c-bead-82c6e69a5b71

jsondag, 2024-04-21:
It’s just powered from a PC at the moment. So that could be the problem.

Shaztech, 2024-04-21:
If you get a good 5.0V at the LED module, maybe your WS2812B is faulty, they are really sensitive (or cheaply made), so the heat when you soldered it can have killed it.

I'm thinking of where to put the timeout choice (limited space in the setting menu), or if I simply change it to 15 sec when the mute button is active. Since the mute is usally used when you are in an environnement where you don't want to disturb.

Shaztech, 2024-04-21:
Also from your video I can see that when it's flashing it's amber (that's green + red) so the green is stuck.

jsondag, 2024-04-21:
Multiple setting pages maybe?  There are likely other things that could be added down the road. Also, a page to show IP would be good. You currently only see it when you connect. I had to check DHCP leases on my router to find it again.

Shaztech, 2024-04-21:
When you start it, it's showing on the loading screen ;)

Shaztech, 2024-04-22:
I will add a button to turn off the screen manually
[image]

Shaztech, 2024-04-23:
Try this
[PillDispenser.esp32.v1_4.zip](https://github.com/Shaztech/Pilldispenser/files/15070019/PillDispenser.esp32.v1_4.zip)

mrperson2015, 2025-01-12:
I'm experiencing the same issue. The LED remains green constantly, only turning off a few seconds after the screen turns off.

This is happening with version 1.8, even after performing a factory reset. I've also tried a fresh installation using esptool. To rule out hardware issues, I tested another board I had set aside for a new dispenser. After loading it with the same software, the LED on the back behaves the same way.

The voltage to the LED board (from jsondag) measures 4.71V.

Shaztech, 2025-01-13:
I get the same problem, sometimes the LED turns green for no reason. I've tried to change some things in the code (before version 1.8) and still the problem persist.
I don't know how to fix this. 
If someone want to help, that would be great.

mrperson2015, 2025-01-13:
Perhaps @Shaztech can provide some guidance on remotely debugging the code. I'm new to microcontrollers but have experience with general coding and remote debugging. I’ve already set up the project and have it running in Arduino IDE 1. I can write and upload code successfully, but I need assistance with the debugging process.

Shaztech, 2025-01-13:
Check everywhere "pixels" is called. 
I'm using the library Adafruit_NeoPixel.

It's also normal that every change of the LED is made on 0 and 1
Ex:   
pixels.setPixelColor(0, pixels.Color(213, 230, 255));
pixels.setPixelColor(1, pixels.Color(213, 230, 255));

Because if you don't use the small driver board, you can use 2 LED Chip, the first one as a sacrificial LED.

mrperson2015, 2025-01-13:
@Shaztech, is there any way of enabling logging?

mrperson2015, 2025-01-13:
I have the serial debugging in place now. I can trace things now. Will take some time complete. I will report back w/ my findings. Thanks again for the project and the help.

Shaztech, 2025-01-14:
I think it's an hardware issue or a bug in the library version

jsondag, 2025-01-14:
I had this issue initially, but after doing an ota update it stopped happening. Though that was several releases ago.

mrperson2015, 2025-01-14:
It is happening even after I erase the flash and load from cmd using the release files. I suspect it is hardware related. I dont know enough about electronics to test the led board for errors. I cant imagine it is happening on 2 different ESP32 boards and causing the issue.

Shaztech, 2025-01-15:
Can you try to power the LED board with an external 5.0 to 5.1v
Too see if the voltage is too low.

jsondag, 2025-01-15:
If you power the board from an external supply, make sure the ground of your esp AND the ground of the supply are tied together. Then make sure only your supply positive is tied to the positive of the led board.

I would first measure the voltage at the ground and positive pins directly on the led board, if it's 5V then testing with an external supply would be unnecessary.

Technically minimum supply voltage for the chip on that board is 4.5V, but it's possible you have a bad chip. If you got it from me, I'll replace it, if it's bad.

When I had this behavior, my voltages were fine. I haven't watched closely to see if this happened again, as I usually walk away after dispensing, but I'll watch for it over the next few days.

mrperson2015, 2025-01-15:
I get anywhere between 4.6-4.71v measured from the pins on led board as powered from the esp32. I removed the positive pin from the board and added a positive and negative to the other side from an external 5.1v power supply. It acts the same. Intermittent behavior on the greenish light. darn it. @jsondag, I will be ordering a new board. I will send you an email. 

Thanks for all your help.

mrperson2015, 2025-01-18:
We should close this issue unless you want to wait to verify against a new LED board.

closed 2025-02-03 by Shaztech

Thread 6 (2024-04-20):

Shaztech/Pilldispenser #6: Servos

bnred777, 2024-04-20:
Hello, I purchased some servos from aliexpress that were supposed to be towerpro sg90 servos. Seems they might not be exactly the same as to what you have used. I can't seem to install the server because it is a bit too tall. I measure about 1.5 to 2 mm of gap between the servo and tray mount face where the screws go. 

Could you please provide the measurement of the servos that you actually used as described here in measurement "F" in the following link? https://www.towerpro.com.tw/product/sg90-analog/

Also, would it be possible to get a link to where you purchased for servos the project?

Thank you in advance, I'm really looking forward to completing the project. Excellent work!!!

Shaztech, 2024-04-20:
I've had this issue on some servos I got from Aliexpress, you can use them "as is" without screwing too much. The new arm (2 weeks ago) accomodate for the shorter/taller servos.

closed 2024-04-20 by Shaztech

bnred777, 2024-04-20:
Thank you! After looking at your images I believe you are using analog servos correct?

Shaztech, 2024-04-20:
I don't understand you question.

I based my design on SG90 servo model I found online (grabcad) and it was the same with some I had here (old stock). So I don't know if there was a revision or it's just different from any manufacturers. I've seen some picture of another user tray and it was fitting perfectly.

bnred777, 2024-04-20:
Oh I see, tower pro supplies a digital version of the SG90 as can be see on their website here: 

https://www.towerpro.com.tw/product-category/servos-parts/micro-servo/

I too am not 100% of he difference but I would assume one is designed for serial communication vs a standard analog version that uses voltage to determine where it need to position. I believe you are using PWM in your code so that would mean the analog version is the correct one (I think at least)

Shaztech, 2024-04-20:
Yes I use the "standard" PWM (Analog) version. The one you can buy for 2$ everywhere XD

bnred777, 2024-04-20:
Perfect, thank you again!

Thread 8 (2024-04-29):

Shaztech/Pilldispenser #8: No LED display

RoboCop0815, 2024-04-29:
In my case, the LED shows nothing, neither RED nor green or anything else.
But the 74AHCT125N gets very warm (about 70°C/150°F), is that normal?

Where is my error?

Shaztech, 2024-04-29:
The IC is not a 74AHCT125N but a ATTiny414.
The orientation of the IC seems ok, try a new board with new components.
You can also try with a strip of WS2812B of 2 leds (without the board and the 75A...) and cover the first led with black tape.
This board is only to raise the signal level (data in) from 3.3v to 5v

RoboCop0815, 2024-04-29:
thanks, I have tried it with the 2 x WS and the LEDs do their colors as it should, only now I have no more alert... Is that normal?
or have I torn off a cable, lol

Shaztech, 2024-04-29:
The first LED can sometimes act weird (lower voltage on the data pin) that's why I said to cover it with a black tape.

RoboCop0815, 2024-04-29:
I just put them in a heat shrink tube..lol

Shaztech, 2024-04-29:
That will do better than the tape !

closed 2024-04-29 by Shaztech

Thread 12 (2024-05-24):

Shaztech/Pilldispenser #12: Detailed Compile instructions with Arduino IDE

ibgregr, 2024-05-24:
So I set up the Arduino IDE to use the "ESP Dev Board" as everywhere I read it said to use that (or any other ESP variant).  But when I try to compile the Sketch I get the following:

Sketch uses 1691373 bytes (129%) of program storage space. Maximum is 1310720 bytes.
Global variables use 116384 bytes (35%) of dynamic memory, leaving 211296 bytes for local variables. Maximum is 327680 bytes.
Sketch too big; see https://support.arduino.cc/hc/en-us/articles/360013825179 for tips on reducing it.
text section exceeds available space in board

Compilation error: text section exceeds available space in board

I'm not sure if I have the incorrect board settings or what.  I tinkered with the "Partition settings" and got it to compile but I'm not sure I even chose the right entry there either.  I would like to have some more detailed steps on how to compile and directly upload to the board from the IDE (if it's even possible).  If not, the steps to generate the bin files like you have to upload with esptool.  Nothing I have tried has worked and I end up having to just reflash your bin files.  It's been YEARS since I have messed with any Arduino type stuff and my old brain has purged all of that knowledge.

Also, the readme section about loading the bin files references a file called boot_app0.bin which is not one of the bin files you have.  And the esptool command does not reference all 5 bin files that were downloaded.  Can you clarify exactly what should be used to reflash the board?

So..to sum it up.  I would like to know if it's possible to compile and upload the app from the Arduino IDE...and if so...what are the board settings, etc I need to use.  If that's not possible, can you give detailed steps on how to produce the bin files and the detailed steps to upload it.

Thanks for such an awesome project!!

GregR

Shaztech, 2024-05-24:
[image]

Use the minimal spiff setting under partition scheme !

[image]

Also if you want to create a bin file use the "Export compiled binary"

Shaztech, 2024-05-24:
for the spiff data file you need to click "ESP32 Sketch data upload", the file will be in the temp directory.
[image]

If the light turn on a few seconds it means the code is running, only the LCD isn't showing.
Did you copy all the library files into your documents ? 
Because there's a config file in the TFT_eSPI that is special for this LCD module.

ibgregr, 2024-05-24:
Yes..I copied the libraries and PillDispenser folders from your Pilldispenser-1.5.zip file to my Documents\Arduino directory.  The libraries folder has the lv_conf.h file which is what I think you are referencing above.  So I should have exactly what you have in the zip file.  This compiles just fine and uploads but again the LCD never comes on.  Just the LED for a bit and then it goes off as well.  Are you sure the zip file is as expected?  Also, I do not have the "ESP32 Sketch Data Upload" menu item.

Something is not quite right here...

ibgregr, 2024-05-24:
Ok...I'm using the v2.x of the Arduino IDE and have found the Upload ESP32 Sketch Data may not work...but...I have found the tool to recreate the SPIFF files so all is good there.

As for the other files.  I have EXACTLY what came from your PillDispenser-1.5.zip file.  You state you included all of the libraries you are using but I have found that the UniversalTelegram library is not in the libraries directory and had to be installed so I'm wondering if the zip file is complete?  I'm assuming I should be able to copy the PillDispenser and libraries folders to my Documents\Arduino folder and compile/upload this to the board and it should work.  But that is not the case.  The code compiles and uploads but the LCD display does not come on.  Any other ideas?

ibgregr, 2024-05-24:
It might help to list the version of each library you are using so that I get the same ones installed.  I say that because it looks like some of this is version dependent.  For example, with the latest version of lvgl installed the code will not compile at all.  And, there's an include in the Adafruit_PWM_Servo_Driver_Library for "#include <Adafruit_I2CDevice.h>" which cannot be found but if I upgrade that library then it is good...but then that requires another library that it installs.  

Anyway...I will wait to hear back on what you find.  I'm thinking it's as simple as a missing file, out of date file, etc that is causing this which means the source zip file is not in sync with your build system.

ibgregr, 2024-05-24:
A bit more troubleshooting I've done.  

1. I copy the PillDispenser and libraries folders to my Documents\Arduino folder and click upload, the compile actually fails due to missing UniversalTelegramBot library and missing files for the BusIO library which is used by the Adafruit_PWD_Servo_Driver Libary.

2. I install the UniversalTelegramBot library (latest version) and the Adafruid_BusIO library (also latest version) then I click upload.  The compile completes successfully, and then the code is uploaded to the board and it reboots.  The LED comes on white and the LCD display flashes when it is updating the strings.  I can see it flash for each of the "Servo lock" messages that would have been displayed but then it ends up off.  So this has to be something that is not configured correctly in the source files provided or it could be a library version issue with the Adafruit_BusIO library that I had to install.

Maybe it would be better to just recreate the source files directly from the system where you built the bin files for v1.5.  Or if you have access to a clean system then you could try copying those folders and see if you can build and upload it to a board and have it work properly.

Thanks again for helping with this.  I just bought you 3 coffees as well!

Shaztech, 2024-05-24:
I use arduino 1.8.19 (I really do not like the version 2.x).
Here's my FULL library (there's stuff you don't need, but it's for testing), I can compile without any problem with this and it work fine.

https://1drv.ms/u/s!AhrI-O28GqX7ia0-orkJlkawpzfHiQ?e=N0E8ff

ibgregr, 2024-05-24:
Ok...I tried that first with the IDE 2.x.  Same results.  I then uninstalled the 2.x and installed the 1.8.  Same results.  Then I totally uninstalled the Arduino "stuff" and removed all directories.  Reinstalled IDE 1.8 and it worked!  Then I tried to install 2.x and it did not work (screen flashes, etc).  Uninstalled 2.x and went back to 1.8 and it is still working.  I removed all of the unneeded libraries for now.  My next test later tonight will be to take your 1.5 zip file and see if that works.  I would really like to figure out why 2.x code does not.

Shaztech, 2024-05-24:
Like I said, I don't like 2.x, the interface is weird for me, simpler with 1.8.x. The constant "updates" it want to do with the libraries (I use older versions sometimes because newer break stuff). So I cannot help with 2.x. But I know that you can use a Portable version of 1.8.x and it doesn't mix libraries (libraries stays in the portable folder).

ibgregr, 2024-05-25:
First of all...I'm not sure what was going on with the libraries.  I still think something is slightly different between what was in the 1.5 zip file and the libraries your local library.  As I stated above, I cleared out everything from that library folder except for the ones required by PillDispenser.  I also have this working fine with IDE 2.x.  I believe some of the issues I was seeing was due to the way things are cached.  Once I totally removed ALL remnants if both Arduino IDE's (and any leftover directories) and reinstalled 2.x it worked...but only when I used the libraries from your local copy.  So that is what I'm going to stick with for now.  I may try to do some kind of folder compare to see if I can find what is different from the 1.5 zip and. your local libraries...but that's a task for another day.  Once again, thanks for sticking with me on this.  I understand you like the 1.8 IDE but it just feels too dated for me after doing most of my coding in Visual Studio (C#, etc).  I agree with you about the annoying popup about library "updates" every time I start the IDE...but that's a small price to pay for progress...I guess. :)

ibgregr, 2024-05-25:
Guess I should have search before I mentioned the "updates" above.  This site tells you how to disable that check on startup so that it does not pop up:

https://forum.arduino.cc/t/i-need-to-prevent-arduino-ide-2-x-from-checking-for-library-updates/1190545

Shaztech, 2024-05-25:
Thanks, will check.
I've updated the libraries folder, added Universaltelegram.
You can check if they are ok

ibgregr, 2024-05-25:
If you want the libraries to be complete you also need to include Adafruit_BusIO and ArduinoJson.  The first one is a dependency for the Adafruit_PWM_Servo_Driver_Library and the second is a dependency for UniversalTelegramBot.  If you add those then you will have everything.

Shaztech, 2024-05-25:
Done

closed 2024-05-25 by Shaztech

ibgregr, 2024-05-25:
Ok..just replaced my libraries folder with a clone from here and it compiles, loads, and runs just fine.  I guess you would need to udpate the tar and zip files that are on the binaries download page so that they have the correct libs as well.  Thanks for getting all of this cleaned up and synced!  I also found a plugin for IDE 2.x that provides the sketch data upload as well.  It just goes out and runs mkspiffs to create the image and then uploads it to the board.  So I have everything working with IDE 2.x now.  Have a great weekend!

ibgregr, 2024-05-25:
One more thing...did you use Squareline Studio to build the UI?  If so can you share the .spj file(s).  I would like to tweak a few things for my own liking without having to figure it all just by looking at the code.

Shaztech, 2024-05-25:
I think you remove your last question, so you probably just found it ?

ibgregr, 2024-05-25:
Yep...as soon as I clicked the button I saw it in the repo :)

jsondag, 2024-11-22:
Hello. Trying to make changes for a version of the software for testing out servo boards. I have my test jig set up, so I can place a board on pogo pins, and use it with modified firmware that actuates all the servos, and then runs the LED through all the colours, when I press the screen off button. 

I was looking into changing the interface a bit to have buttons for each servo on the main screen as well is individual buttons to test all servos, the LED board, and play either file 1 or 2 on the dfplayer.

How do you prepare the asset files for upload? I'm just starting to play around in squareline studio.

Shaztech, 2024-11-22:
[image]

After you modified the Squareline project click on Export UI Files, it will create an arduino folder. Replace the files in the "C:\Users\user\Documents\Arduino\libraries" Probably the folder "ui"

Also, in the Arduino files, you need to add your button event (in the PillDispenser.ino):
ex:  lv_obj_add_event_cb(ui_VolTestBTN, VolTestBTN_event_handler, LV_EVENT_ALL, NULL);
but replace the name with the button name

and the void that do the action (in the LVGL_Buttons.ino):
ex:
static void VolTestBTN_event_handler(lv_event_t * e) { // Test Volume Button
  lv_event_code_t code = lv_event_get_code(e);
  if (code == LV_EVENT_CLICKED) {
    spkvolume = lv_slider_get_value(ui_VolSlider);
    Playsound(2);
  }
}

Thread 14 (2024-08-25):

Shaztech/Pilldispenser #14: Automatic pill throw out by alarm?

panthermatrix, 2024-08-25:
The automatic pill dispenser is good project. With the title, however, I assumed that the pills would or could be ejected automatically, not just an alarm sounded and the throw out had to be confirmed manually on the display.

I would be happy about a function or setting, also optional as far as I am concerned, that gives the alarm, but also throws out the pills of the respective compartment directly. In addition, it should not be necessary to end the alarm by touch with automatic ejection.

Would that be feasible?

burkby, 2024-09-05:
I would also like to have this option.

I have a father-in-law with Parkinson's and Dementia, so I am not sure if he can press the touchscreen to dispense. 

I can see some drawbacks of it. My father-in-law takes meds four times a day. Once with breakfast, once after, in the evening and before bed. I could see a situation where he'd easily combine doses.

Maybe, adding to the idea of auto-dropping, we could do something remotely via Telegram. I haven't gotten Telegram to work yet.

So far, this is sitting on my desk, I just have it set up today and will be testing with skittles or smarties.

Shaztech, 2024-09-05:
The problem with that is the "Multi-user" aspect of the project. If I make an "auto-throw" option it will interfer with that and mix pills into the chute. Also if the pills are not taken at the time of the alarm and multiple alarms occur (ex. the person is not home for the day), it will mix them all in the chute. It can be really dangerous.

The best option would be to add a large physical button on the side (or modify the base to fit it somewhere) and add a input pin to act as "Dispense"

[image]

burkby, 2024-09-06:
I like the idea of adding a physical button. I don't have the knowledge to do this but it's something that I will look into for sure. 

The auto drop idea has its drawbacks with potentially adding extra doses like you mentioned.

I don't use it for multi-user, it's a singular user in my scenario.

Also wanted to say thanks for making this device. It's a great piece of tech.

Shaztech, 2024-09-06:
I can add that to the code and show you where to solder the wire for the momentary switch signal + ground.

panthermatrix, 2024-09-06:
I made an easier solution myself since I am using ioBroker and other Smart Home controlls. The file **Web_Stuff.ino** from the source code here can also listen for external commands and the ESP32 board is very powerfull. So you can open an url on the pill dispenser and force drop out. This can be done with every web client like smartphone. For automation ioBroker or similiar software with script functionallity may help.

However, I recommend regularly checking whether the pill has been dispensed. There may be a mechanical defect, for example. It is therefore advisable to memorize the number on the label or note it in the ioBroker script or whatever and compare it after the drop-out. This way you can at least make sure that the pill has been dispensed. However, a mechanical button would have the same problems, as dementia can cause forgetfulness.

**Note:**
_A functionallity for forcing alarm sounds as a reminder on url call would be another idea, but I did not find the code for it yet._

**URL call is like:**
http://[ip_of_pill_dispenser]/droput?tray=[number_of_tray]

**Example:**
http://192.168.178.22/dropout?tray=1

Here is my code suggetion:
I added this at the start of "void webroute()" at line 415:

```
const int NUM_TRAYS = 10;

void webroute() {
  
  server.on("/dropout", HTTP_GET, [](AsyncWebServerRequest * request) {
    if (!request->hasParam("tray")) {
      request->send(400, "text/plain", "Param 'tray' is missing.");
      return;
    }
  
    int tray = request->getParam("tray")->value().toInt();
  
    if (tray < 1 || tray > NUM_TRAYS) {
      request->send(400, "text/plain", "Wrong value for tray.");
      return;
    }
      
   dispense(tray);
   request->send(200, "text/plain", "1");
 
  });

// the rest of the code ...
```

Shaztech, 2024-09-06:
Nice, thanks for that. I will also add it in the code as an option in the next update.

panthermatrix, 2024-09-06:
Perfect, thank you!

Perhaps this option can then be "External control via web service" or something similar.

I can think of two extensions, one is the one mentioned above and one is the alarm.

- http://[ip_of_pill_dispenser]/droput?tray=[number_of_tray]
Dropout pill from selected tray
- http://[ip_of_pill_dispenser]/alarm
Shows the alert screen „Take your pills“ with alert sound

**Idea for a button**
An external wireless button such as a Zigbee button from Ikea can be integrated into the local smart home network and either eject the pills when buttons are used (http://[ip_of_pill_dispenser]/droput?tray=[number_of_tray]) or delete an returning alarm (http://[ip_of_pill_dispenser]/alarm) if, for example, it is to be ensured that the pills are taken.

But this has nothing to do with the pill dispenser, it is an external script e.g. ioBroker. But the functionality to remotely control the pill dispenser would make this possible in the first place.

Shaztech, 2024-09-06:
I will probably add also this:
http://[ip_of_pill_dispenser]/droput?dispense

This command will drop the pills that are currently in alarm. And return an error if there's no active alarm.
So I can make a external button that replicate the "Dispense" touch, with a cheap ESP8266 and a button.

panthermatrix, 2024-09-06:
Good idea.

panthermatrix, 2024-09-07:
I have another suggestion. Sometimes during hot temperatures some trays may not work as expected. Here a /fix remote should be also implementet to fix stuck on half.

**Url can be like:**
http://[ip_of_pill_dispenser]/fix?tray=[tray]

**And my suggestion for /alam:**

**File: Dispense_Routine.ini:**
Add new method at the top:
```
void playAlarmSound(int id) {
  lv_timer_reset(alertsound_timer); // Reset alert sound timer
  Playsound(id); // Play the alarm sound
}
```

**File: Web_Stuff.ino**
Add between void webroute() { ... }:
```
  server.on("/alarm", HTTP_GET, [](AsyncWebServerRequest * request) {

    int alarmId = 2;
    if (request->hasParam("id")) {
      int alarmId = request->getParam("id")->value().toInt();
    }
  
   playAlarmSound(alarmId);
   request->send(200, "text/plain", "1");
  });
```

**You can use it like:**
- http://[ip_of_pill_dispenser]/alarm
This will play default alarm (number 2)
- http://[ip_of_pill_dispenser]/alarm?id=[custom_id]
This will play any sound beginning with the custom_id

Shaztech, 2024-09-07:
I was currently modifying the code. I've added the following:

http://[ip_of_pill_dispenser]/alarm    (Play the default alarm #1)
http://[ip_of_pill_dispenser]/alarm?id=[custom_id]      (Play the alarm #)
http://[ip_of_pill_dispenser]/dispense     (Dispense the current tray in alert, does nothing if there's no alarm)
http://[ip_of_pill_dispenser]/droput?tray=[number_of_tray]    (Drop the pill in tray #)
http://[ip_of_pill_dispenser]/dismiss       (Dismiss current alarm that are in progress)
http://[ip_of_pill_dispenser]/fix?tray=[number_of_tray]       (Make half step to fix tray #1 

GPIO4 can be pulled low to dispense the current tray in alert, does nothing if there's no alarm.

Fixed the typo in the tray config page: "Tray Pos. Adjustment:" -> "Tray Pos. Adjustement:"

I will upload the bin file here for you guys to test it.
Thanks again for your suggestions.

panthermatrix, 2024-09-07:
Thank you very much.

Shaztech, 2024-09-07:
Here is the beta version 1.7:

https://1drv.ms/u/s!AhrI-O28GqX7io8854s59nB6QsriPA?e=KMYMWu

Please try every "options" and tell me if it's ok !

panthermatrix, 2024-09-07:
I testet the PillDispenser.esp32.v1_7Beta.bin version via OTA. One thing does not work:

- http://[ip_of_pill_dispenser]/alarm (Play the default alarm no 1)
- http://[ip_of_pill_dispenser]/alarm?id=[custom_id] (Play the alarm "id")

**/alarm?id=[custom_id]** does not play a different alarm. If I type /alarm?id=3 or /alarm?id=4 it always plays the same alarm as /alarm does (filename: 2-xyz.mp3).

Can you please check if the **id** if set is recognized?

Shaztech, 2024-09-07:
It's supposed to work, I don't see anything wrong with the code.
Do you have more than 2 mp3 on the sd card ?
Does it play the first mp3 if you type /alarm?id=1 ? (Since the default alarmId is 2)

panthermatrix, 2024-09-07:
I have got 6 files on SD Card, all starting with the number. The both default files and:

- 1-Alert.mp3
- 2-PillsReady.mp3
- 3-Alarm1.mp3
- 4-Alarm2.mp3
- 5-Alarm3.mp3
- 6-Alarm4.mp3

but no matter what I enter as id, it will always 2-PillsReady.mp3 played.

I testet also:
/alarm?id=1

panthermatrix, 2024-09-07:
Now it works perfectly.

While testing the boot problem whith stuck on time sync #15 did not appear anymore.

Thank you very much.

closed 2024-09-07 by panthermatrix

Shaztech, 2024-09-07:
Did you test the with the physical input (GPIO4) ?

panthermatrix, 2024-09-08:
No, only the new remote functions yet. I can not test the physical inputs at the moment, since the pill dispenser is in use. But I will build another one as replacement and for testing soon.

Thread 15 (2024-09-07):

Shaztech/Pilldispenser #15: Sometimes cold boot stucks at time sync ...

panthermatrix, 2024-09-07:
If I turn on the device after a while after a power disconnection and the time synchronization is activated, it sometimes happens that the boot process stops at "Syncing time..." stuks.

I was also able to understand this by a soft reset. Why this is the case is not entirely clear.

That's why I built in a second attempt as a solution and if this also fails, a reboot of the device. After the soft reboot, it has always worked so far.

But I could imagine that e.g. if there is no internet connection, a boot loop will be created here with my code suggestions. Do you have any idea how to avoid this? My suggestion here is to store a value like "reboot_on_timesync_fail = true" and to do without synchronization in case of failure despite soft reboot. A successfull rebot will set this value to reboot_on_timesync_fail = false.

Here's my code so far that works for me.

In file Loading_Screen.ino replace the void setupTime():

```
void setupTime() {

  int dsttemp;
  if (dstEnabled) {
    dsttemp = 3600;
  } else {
    dsttemp = 0;
  }
  configTime(utcOffset * 3600, dsttemp, "pool.ntp.org", "time.nist.gov");

  // Set time for first try
  unsigned long startTime = millis();
  unsigned long timeout = 10000; // Set to 10 seconds

  struct tm timeinfo;
  while (!getLocalTime(&timeinfo) && millis() - startTime < timeout) {
    Serial.print(".");
    delay(1000);
  }

  //
  int retryCount = 0;
  while (!getLocalTime(&timeinfo) && retryCount < 2) {
    Serial.println("Time synchronization failed. Try again...");
    delay(5000); // Wait for 5 seconds
    retryCount++;
  }

  // If all attempts have failed, perform a reset
  if (!getLocalTime(&timeinfo)) {
    Serial.println("Time synchronization failed. Perform a reset...");
    ESP.restart();
  } else {
    Serial.println("Time synchronized");

    // You can now use time functions like localtime_r to get current time
    char strftime_buf[64];
    strftime(strftime_buf, sizeof(strftime_buf), "%c", &timeinfo);
    Serial.print("Current time: ");
    Serial.println(strftime_buf);
    
    update_time_label(NULL);
    lv_timer_create(update_time_label, 15000, NULL); // Update every 15 Sec
  }
}
```

Shaztech, 2024-09-07:
I've never encounter that issue and I use my device daily. I've restarted it A LOT OF TIMES when I was testing and never had an issue with time sync. If there's no wifi, it just boot without clock. Maybe there's a problem with your acces point, or internet ?

panthermatrix, 2024-09-07:
Could be possible, but I have the problem even when I put the pill dispenser right next to the WLAN router. The wifi router uses WPA2/WPA3 and all other devices do not have problems connecting. The web ui of this devices works perfectly and never stucked. So wifi connection of this devices works. I also tried differend usb power plugs with more power 2.4A or iQ or other loading types.

1. The pill dispenser first connects to wifi -> successfull
2. pull dispenser shows correct IP
3. pull dispenser tries to sync time -> sometime it works, sometimes it does not work

Internet connection is working fine and also the time server are pingable.

This is kind of strange, but a soft-reboot always worked for me.

Shaztech, 2024-09-07:
I've changed the code like that:

  int dsttemp;
  if (dstEnabled) {
    dsttemp = 3600;
  } else {
    dsttemp = 0;
  }
  configTime(utcOffset * 3600, dsttemp, "pool.ntp.org", "time.nist.gov");

  // Wait until time is synchronized
  Serial.println("Synchronizing time");
  struct tm timeinfo;
  unsigned long startTime = millis();  // Record the start time

  while (!getLocalTime(&timeinfo)) {
    if (millis() - startTime > 30000) {  // Timeout after 30000 milliseconds (30 seconds)
      Serial.println("Time synchronization timed out.");
      break;
    }
    Serial.print(".");
    delay(1000);
  }

  if (getLocalTime(&timeinfo)) {
    Serial.println("Time synchronized");
  } else {
    Serial.println("Failed to synchronize time.");
    ESP.restart();
  }

I've made a 30 sec timeout. (it's safer that way)

If it cause any problem tell me. It will be with be with the bin "1.7" in the other issue

panthermatrix, 2024-09-08:
I think it works with this new code now. After several restarts the problem seems to be gone.
Thank you.

closed 2024-10-28 by Shaztech

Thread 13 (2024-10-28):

### ISSUE TITLE
24 hours clock question + generic pill taking question

### ISSUE THREAD

**Issue by gitterman** [Shaztech/Pilldispenser#13]
I am in the process of building your ingenious project and found that the web interface shows a 12-hour clock, whereas the LCD shows a 24-hour clock.
My PCs and my phone are US English because of business use, but I'd like to have an unambiguous 24-hour clock on the web interface too. Is that possible?
For the general understanding: 
  If I have to take pills A in the morning, pills B at noon, pills C in the afternoon and pills D at bedtime, how do I set need to set this up?
  Do I need 4 separate trays just for me then?
  Or is it possible to put 4 alarms on the same tray in 4 different slots?

**Comment by Shaztech** [comment]
![image](https://github.com/user-attachments/assets/53d80cd3-4575-497a-95da-ceee65ef6d8b)
The web interface is already in 24h format. Maybe it's OS dependent (Windows clock settings)
Yes 4 trays, because the goal of this device was to refill it only once per month (30 days).
It will be a pain to refill certains tray after 7 days others 10 days, etc.

**Comment by gitterman** [comment]
Thanks for the quick answer.
I did run the web interface on my android phone.
For the tray issue, I understand now.
It is a pity, though, if you need to take pills only for a certain amount of time (less than a month).
E. g. I got prescription of cortisone for 14 days and I need to take a pill for stomach protection an hour before I take the cortisone pills.
Nonetheless, I understand your point of view and if I have time I will check if I can tailor the code for my needs.
BTW: there is a slight typo on the LCD screen. When you adjust the slot, the message says "adjustement" instead of adjustment.

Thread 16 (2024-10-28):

### ISSUE TITLE
Feature Request - signal-cli-rest-api integration

### ISSUE THREAD

**Issue by agentdr8** [Shaztech/Pilldispenser#16]
Great project you've got going here. All of my 3D printed parts are done, and have received my PCBs. Just waiting on components for the time being. 

Taking a look at the functionality, I see that there is built-in Telegram notifications, using the UniversalTelegramBot library. Would it be possible to include Signal integration, by way of the [signal-cli-rest-api](https://github.com/bbernhard/signal-cli-rest-api)? I have that Docker container running within my network, and would love to be able to fire off notifications via Signal. It could even support per-user or per-tray notifications. 

Since it's just HTTP requests, it shouldn't require any additional libraries, just some code additions. If it's out of scope for what you want to implement, I might be able to submit a PR.

**Comment by Shaztech** [comment]
I can add it, but only I you can send me the code for that portion.
I also have no mean to test it.

Thanks

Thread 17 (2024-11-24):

### ISSUE TITLE
Is there any way to convert the project to raspberry pi

### ISSUE THREAD

**Issue by bob5731** [Shaztech/Pilldispenser#17]
I was thinking about using a raspberry pi 3B+ to run the project. I tried compiling it on a MacBook Air early 2011 running 10.15.7 but it refuses to compile due to incompatibility issues with the offering system being too old. I don't currently have my Arduino boards where I'm at so I'd like to see if there's a way that I can use an emulator or something else to run the project and see if it will meet my needs before printing all of the parts. Would also help if you could drop all the parts into single STL files and then zip them up.

**Comment by Shaztech** [comment]
Too much job and I don't know linux that much... It's made for an ESP32 with a touch screen. It's not a "software" it's directly hardcoded for the hardware. Also if you want the stl, go to makerworld (with the link) to download them.

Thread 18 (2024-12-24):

Shaztech/Pilldispenser #18: Not an issue - just a question!

clucluclu, 2024-12-24:
Hi, this is a really impressive project!

I’ve been looking at how I can build an automated pill dispenser and integrate it with Home Assistant (popular home automation platform) to allow me to fire automations and alerts based on pill taken/not taken status, and refill readiness. Initially I was thinking easiest thing to do would be to use your hardware build, but use an esp32 running esphome instead and replace the logic entirely (mainly because I am familiar with coding for esp home and it integrates nicely with Home Assistant).

However, your code and project is so mature, that I’m wondering if I’m better off trying to simply make your build entirely and adding a few lines to the Arduino code so that it works as you intended, but also allows some information to be exposed to Home Assistant.

Various ways this could be achieved I suppose (and unsure if you or anyone else has ever considered same) - but before I give it a crack a do you have any advice/recomemndations you can share that might make it easier for me? -

- which variables will make the most sense for me to track?

- at which point in the codebase (ie which routine) would it make the most sense for me to call/embed my extra functions to ensure I get a real time feed as things change?

- is there is already some method baked in that allows for real-time access to this data over local network (prefer not to scrape the web interface if there is a way to get it more cleanly - though a simple REST style API would make it very easy.

- If you have any other good ideas or recommendations I’d love to hear them…you are already my hero for making such a polished project!

Thanks again - Clu.

Shaztech, 2024-12-24:
In the latest version I already added some actions that can be made with a web interface:

http://[ip_of_pill_dispenser]/alarm (Play the default alarm no 1)
http://[ip_of_pill_dispenser]/alarm?id=[custom_id] (Play the alarm "id")
http://[ip_of_pill_dispenser]/dispense (Dispense the current tray in alert, does nothing if there's no alarm)
http://[ip_of_pill_dispenser]/droput?tray=[number_of_tray] (Drop the pill in tray "number")
http://[ip_of_pill_dispenser]/dismiss (Dismiss current alarm that are in progress)
http://[ip_of_pill_dispenser]/fix?tray=[number_of_tray] (Make half step to fix tray "number")

for the variable to monitor, probably theses:

bool trayAlertEna[11] (is the tray is enabled for a daily alert)
bool traytriggered[11] (is the tray is currently in alert)
bool trayEnabled[11] (is the tray is enabled "installed")
bool traydisptoday[11] (is the tray has beed dispensed for today)
bool traydismtoday[11 (is the tray has been dismissed for today)

you can probably make your calls on the "Check_Alerts.ino" file. It's called every minute to check for alerts.
or you can modify "Web_Stuff.ino" and make requests for each info you need with HA via web requests.

no there's no method baked yet, but if you want to modify it, you can create a fork or include you modifications and I can add them in the next version ;)

I don't have HA yet, I'm still using an old version of Blynk with my own server (before they changed to subscription...)
I'm too lazy to change all my devices codes to switch (over 44 devices) XD

Thanks !

Shaztech, 2025-01-03:
check the v1.8 update, a lot of calls can be made:

Actions:

http://[ip_of_pill_dispenser]/alarm 						Play the default alarm no 1
http://[ip_of_pill_dispenser]/alarm?id=[custom_id] 	        Play the alarm "id" 
http://[ip_of_pill_dispenser]/dispense 					Dispense the current tray in alert, does nothing if there's no alarm
http://[ip_of_pill_dispenser]/droput?tray=[number_of_tray] 	Drop the pill in tray "number" (1 to 10)
http://[ip_of_pill_dispenser]/dismiss 					Dismiss current alarm that are in progress
http://[ip_of_pill_dispenser]/fix?tray=[number_of_tray] 		Make half step to fix tray "number" (1 to 10)

Informations:

http://[ip_of_pill_dispenser]/tr_name?id=[number_of_tray]	Return name of the tray
http://[ip_of_pill_dispenser]/tr_color?id=[number_of_tray]	Return 0 to 7 for assigned color (check color table)
http://[ip_of_pill_dispenser]/tr_inst?id=[number_of_tray]	Return 1 if tray is installed
http://[ip_of_pill_dispenser]/tr_enab?id=[number_of_tray]	Return 1 if tray is enabled for daily Alerts
http://[ip_of_pill_dispenser]/tr_trig?id=[number_of_tray]	Return 1 if tray is triggered (Alert in progress)
http://[ip_of_pill_dispenser]/tr_disp?id=[number_of_tray]	Return 1 if tray is dispensed for today
http://[ip_of_pill_dispenser]/tr_dism?id=[number_of_tray]	Return 1 if tray is dismissed for today
http://[ip_of_pill_dispenser]/tr_time?id=[number_of_tray]	Return alarm time for this tray

Color table:

0 = 255, 0, 0 = RED
1 = 255, 0, 255 = MAGENTA
2 = 128, 0, 128 = VIOLET
3 = 0, 0, 255 = BLUE
4 = 0, 255, 255 = CYAN
5 = 0, 255, 0 = GREEN
6 = 255, 255, 0 = YELLOW
7 = 255, 165, 0 = ORANGE

closed 2025-01-03 by Shaztech

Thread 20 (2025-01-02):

Shaztech/Pilldispenser #20: Boards with Components Placed?

ssmithTaylor, 2025-01-02:
I'm a total noob in this area but I'd love to build one of these for myself, I'm terrible at remembering to take my medicine. I noticed some of the sites you can use to build the custom board will also do component placement as well, it does add to the expense but it doesn't seem too bad.

I'm not sure what the complexity of this ask is, but would it be possible to provide gerber files that already have the components placed so we can order them fully assembled?

Shaztech, 2025-01-02:
Check in the comments on Makerworld. There is someone that sell electronic
kits already done

jsondag, 2025-01-03:
That would be me. I have all the non printed parts available. Pick and choose whatever you like. 

Email me at 09-snakes.timbres@icloud.com and I can give details. 

This is my price list as of now. 

<p style="margin: 0.0px 0.0px 0.0px 0.0px; font: 12.0px Helvetica; min-height: 13.8px"><span style="font-family: 'Helvetica'; font-weight: normal; font-style: normal; font-size: 12.00px"></span><br></p>

Description | Quantity | Unit Price | Cost
-- | -- | -- | --
Main PCB, with components, smd assembly, loose pin header | 1 | $16.00 | $16.00
USB socket | 1 | $2.00 | $2.00
LED PCB, with components, smd assembly, loose pin header | 1 | $10.00 | $10.00
Tray PCB, with loose pin headers, straight through. | 10 | $1.00 | $10.00
ESP32 2.8” CYD display dev board. | 1 | $14.00 | $14.00
30mm 2W 8ohm Speaker | 1 | $2.00 | $2.00
DFPlayer mini | 1 | $3.00 | $3.00
Servo  SG90 (buy 1 per tray) | 10 | $2.50 | $25.00
P-Touch Number labels, White on Clear (buy 1 per tray) | 10 | $1.00 | $10.00
3mm OD left hand torsion spring (buy 1 per tray) | 10 | $1.50 | $15.00
Ballpoint pen springs x3 (buy 1 per tray) | 10 | $0.50 | $5.00
Tray Screws #2x5/16” (X10) #4x1/2” (x6). (buy 1 per tray) | 10 | $1.50 | $15.00
Base Screws #2x5/16” (X8) #4x1/2” (x8) | 1 | $1.50 | $1.50
Tig Rod (hinges) | 1 | $1.00 | $1.00
128MB micro SD card | 1 | $3.00 | $3.00
  |   |   |  
  |   |   |  
  |   |   |  
  |   | Subtotal | $132.50
  |   | US Shipping | $8.00
  |   | Total | $140.50

<p style="margin: 0.0px 0.0px 0.0px 0.0px; font: 12.0px Helvetica; min-height: 13.8px"><span style="font-family: 'Helvetica'; font-weight: normal; font-style: normal; font-size: 12.00px"></span><br></p>
<br class="Apple-interchange-newline">

Shaztech, 2025-01-03:
@jsondag Can I put this list and you email in the readme ?

jsondag, 2025-01-04:
Sure. No problem.

closed 2025-01-04 by Shaztech

ssmithTaylor, 2025-01-06:
@jsondag, I shot you an email but haven't received a response yet. Can you confirm the email above is correct? Maybe I got caught in your spam filter?

jsondag, 2025-01-06:
Strange. Could you tell me the day and time you sent the email?

ssmithTaylor, 2025-01-06:
Friday, January 3rd, 2025 at 12:42 AM ET

jsondag, 2025-01-07:
It was in fact in my spam filter. Along with three other inquiries. Unfortunately I get a ton of spam. I need to set up some rules to catch these emails. Thanks for bringing it to my attention.

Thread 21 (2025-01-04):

Shaztech/Pilldispenser #21: Compile Error: Missing esp_int_widt.h in library AsyncElegantOTA-2.2.

mrperson2015, 2025-01-04:
I am new to ESP32/Arduino and developing on them. I am trying to setup the coding environment.  Meaning I could have this all wrong. 

**Issue**:
When I try to compile the current code I am getting an error about a missing file found as part of an include for library AsyncElegantOTA.h. Is this missing from checkin but found on your local environment? Maybe I have a wrong version of something?

**Error**: 
> Arduino: 1.8.18 (Windows 10), Board: "ESP32 Dev Module, Disabled, Disabled, Minimal (1.3MB APP/700KB SPIFFS), 240MHz (WiFi/BT), QIO, 80MHz, 4MB (32Mb), 921600, Core 1, Core 1, None, Disabled, Disabled"
Multiple libraries were found for "WiFi.h"
 Used: C:\Users\xxxx\AppData\Local\Arduino15\packages\esp32\hardware\esp32\3.1.0\libraries\WiFi
 Not used: C:\Program Files (x86)\Arduino\libraries\WiFi
In file included from C:\source_code\Pilldispenser\Arduino\PillDispenser\PillDispenser.ino:13:
C:\source_code\Pilldispenser\Arduino\libraries\AsyncElegantOTA-2.2.7\src/AsyncElegantOTA.h:18:14: fatal error: esp_int_wdt.h: No such file or directory
   18 |     #include "esp_int_wdt.h"
      |              ^~~~~~~~~~~~~~~
compilation terminated.
exit status 1
Error compiling for board ESP32 Dev Module.
This report would have more information with
"Show verbose output during compilation"
option enabled in File -> Preferences.

**Steps taken to setup environment**:
1. Cloned the repo
2. Created new branch
3. Installed Arduino IDE 1.8.18
4. Changed "Sketchbook Location" to [root]\Pilldispenser\Arduino
5. Added Additional Boards Manager URL: "https://raw.githubusercontent.com/espressif/arduino-esp32/gh-pages/package_esp32_index.json"
6. Changed board to "ESP32 Dev Module"
7. Changed "Partition Scheme" to "Minimal (1.3..."
8. Added tool for "ESP32 Sketch Data Upload"

Shaztech, 2025-01-05:
Try to downgrate your esp32 version to 2.0.17
[image]

mrperson2015, 2025-01-05:
What did I do wrong that the version you suggested isnt in my list? I have tried many other versions though w/ no success.
[image]

Shaztech, 2025-01-05:
[image]

mrperson2015, 2025-01-05:
You are FAST. I had been filtering it to ESP32 in the Type dropdown. That doesn't show the esp32 by Espressif Systems. Ugh. I have the correct one selected and installed. Compiling now. It is taking longer than it was ;)

mrperson2015, 2025-01-05:
WORKED!!! Thank you

closed 2025-01-05 by mrperson2015

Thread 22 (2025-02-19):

Shaztech/Pilldispenser #22: Servos wont turn to dispense pills

walkeryan, 2025-02-19:
I have everything populated and wired and programmed, my led flashes the correct color but when I try to do anything related to the servos I get nothing. When I plug the servo in it jumps a tiny bit and will self center if I do that repeatedly but that's the only action I get out of it. I've went over all of my components and connections and even reflashed. Any ideas where I can go from here?

Shaztech, 2025-02-19:
Try another USB power supply, check that the wiring for the SCL, SDA are on
the right pins (the colors of the cable that came with your board can be
inverted).

walkeryan, 2025-02-19:
Thanks, I've checked the SCL, SDA and they are correct, also tried 3 different power supplies. I went with the straight through boards and have bridged the first pads in the middle, I'm assuming thats correct but I just want to verify? Nothing in the write up about it. Thanks!

walkeryan, 2025-02-19:
Also, just discovered that the servo isn't centering when I apply power, its just rotating counterclockwise about 1/16th of a turn until it gets the the end and locks up?

Shaztech, 2025-02-20:
The servo just get power that's why is not centering

[image]

Check the straight board. You need to bridge only one for the tray you want (white mark is for tray #1 next is #2). Each tray need to be unique.

Shaztech, 2025-03-01:
I assume your problem is fixed.

closed 2025-03-01 by Shaztech

Chipper2, 2025-03-23:
I'm having the same issue.  I wanted to do some testing before putting it all together because my soldering skills are very lacking.  To the point I messed up the USBC plug but was able to use the power part of the plug. Are the data wires needed if you are only using them for power?

The display works great but when I plug a motor up, nothing moves.  I swapped the SCL, SDA and there was no change.

I do have a question about the straight boards.  I see above that we need to bridge the appropriate span for the trey that it is installed into.  I took a volt meter to test continuity, and as I tested one by one, all of the corresponding pins were connected.  I may not understand the process of making those work.

Thank you for your time and invention.
Chip

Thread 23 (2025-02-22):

Shaztech/Pilldispenser #23: Request for BOM or Component List for JLCPCB

Joshicopter, 2025-02-22:
Hi Shaztech,

First of all, thanks for your great project! I'd love to build it and have the PCB manufactured by JLCPCB. However, I’m not very experienced with soldering, so I plan to order the PCB from JLCPCB directly. To make the process easier, it would be really helpful if a BOM (Bill of Materials) or other compatible component lists for JLCPCB were available. 

Would it be possible for you to provide these files? That would make ordering much more convenient for me (and probably for others as well).

Thanks in advance!

Shaztech, 2025-02-25:
I don't have theses files. You need to create them.

closed 2025-02-25 by Shaztech

jsondag, 2025-02-25:
I have fully populated boards available. Along with all of the non printed parts. 

Shoot me an email and I’ll give you all the details. 

09-snakes.timbres@icloud.com

jsondag, 2025-04-01:
Apologies. This seems to have been caught by my spam filter. I thought I’d excluded keywords, but apparently spam filters run before the rules I’d set. Please let me know if you still didn’t get a reply, as I had a couple in there and I’m not sure which might be you.

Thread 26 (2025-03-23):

Shaztech/Pilldispenser #26: Can't seem to get motors to turn.

Chipper2, 2025-03-23:
I'm having the same issue. I wanted to do some testing before putting it all together because my soldering skills are very lacking. To the point I messed up the USBC plug but was able to use the power part of the plug. Are the data wires needed if you are only using them for power?

The display works great but when I plug a motor up, nothing moves. I swapped the SCL, SDA and there was no change.

I do have a question about the straight boards. I see above that we need to bridge the appropriate span for the trey that it is installed into. I took a volt meter to test continuity, and as I tested one by one, all of the corresponding pins were connected. I may not understand the process of making those work.

Thank you for your time and invention.
Chip

Chipper2, 2025-03-23:
I have also been tring to work on this.  But i'm on a Mac and aren't having much luck.

The first Firmware Installation:

Download the 5 bin files in this release
Download the esptool.exe from here https://github.com/espressif/esptool/releases/tag/v4.7.0
Copy the 5 bin files to the root of the folder (with esptool.exe)
Connect your device (the ESP32 module with the LCD) to your computer via USB
Find the Serial COM port number (in device manager)
open a command line inside your folder and type, change the COM port that match your device (don't forget to change the files version ex: v1.3):
esptool.exe --chip esp32 --port COM4 --baud 921600 --before default_reset --after hard_reset write_flash -z --flash_mode dio --flash_freq 80m --flash_size 4MB 0x1000 PillDispenser.bootloader.v1_3.bin 0x8000 PillDispenser.partitions.v1_3.bin 0xe000 boot_app0.bin 0x10000 PillDispenser.esp32.v1_3.bin 0x3D0000 PillDispenser.spiffs.v1_3.bin

Shaztech, 2025-03-23:
- The USB C data line is for programming, they are optionnal but you need to program it first with the screen outside the assembly.
- For the servos, there's a version of these that are Digital and not PWM (Analog), You need to be sure they are the right type.
- The straight board version need to have ONE solder bridge on each tray like so (the white mark), the first bridge is for the 1st tray:

[image]

- I don't own a Mac, and the procedure is probably different. (port number, you can't run an exe on mac, the command may be different...) Here's a example from chatGPT:

```
install esptool: pip install esptool
list serial: ls /dev/tty.*
Replace /dev/tty.usbserial-xxxxx with the actual port.

esptool.py --chip esp32 --port /dev/tty.usbserial-xxxxx --baud 921600 --before default_reset --after hard_reset write_flash -z \
  --flash_mode dio --flash_freq 80m --flash_size 4MB \
  0x1000 PillDispenser.bootloader.v1_3.bin \
  0x8000 PillDispenser.partitions.v1_3.bin \
  0xe000 boot_app0.bin \
  0x10000 PillDispenser.esp32.v1_3.bin \
  0x3D0000 PillDispenser.spiffs.v1_3.bin
```

Chipper2, 2025-03-23:
I think I figured out the motor part.  Looks like a looks connection.

As far as programming.  I can't seem to get it to connect to a COM port.  I'm fairly certain I have messed up the chip on the back while soldering.  However, it does seem to connect via wifi, and I'm able to program it from there.

What do the new files do?  Is it imperative that I do this part?  If so, I'll probably need to order a new screen.

Thank you for your time.
Chip

Chipper2, 2025-03-23:
New symptom: if I plug in the first motor, it works great, but any motor that I connect after that doesn't work.  If I move #2 down to the bottom, it works, but nothing after that does.  I have tried all motors individually, and they work, but if I stack them, they don't.

Shaztech, 2025-03-23:
If you have programmed at least once and you have access to the firmware update web interface. The only files you need are 
PillDispenser.esp32.v1_8.bin
PillDispenser.spiffs.v1_8.bin
That's the lastest version.

Maybe your powersupply that you use is not strong enough. Or check that your solder points are ok on the top part of the board on the tray

Chipper2, 2025-03-23:
Thank you, yes, it's once again my soldering skills.  Thank you for giving us such a wide section to shoulder.  To the guys that made the controller, you suck!!  No insult intended.  LOL

Thank you for letting me know about the updating over the air.

Chip

Shaztech, 2025-03-23:
When you talk about the controller you mean the screen module ?

Chipper2, 2025-03-23:
Yes, sir, the screen module.  I broke the LED connections trying to get that off.  On the USB C connector, I broke the D+ and D-.  I didn't even try the speaker, lol.  I drilled a hole in the side of the base to gain access to the USB-C to program it and power it, but then I realized I think the power for the motors comes from the external USB-C port.

Obviously, this is no wear your fault, or anyone else's for that matter.  I suck at soldering, and I knew I did, but I took the risk anyway.  For the most part, I have it working, only issue I'm having now is it doesn't advance as well as I thought it should.

[image]

Chipper2, 2025-03-23:
https://github.com/user-attachments/assets/dc3dc41f-e6bf-4138-8d82-023f19e7502f

Shaztech, 2025-03-23:
You need to feed the servo board 5v, you don't have a choice.
The tray should turn without freely (when the lock and motor are not installed). If it's too tight maybe scale it down to 99.5% or something like this. But I didn't had any complain on that.

Shaztech, 2025-03-23:
Try to reprint the arm, there's goop at the base, also does the lock is printed and in place on the other side ? I don't see there

Chipper2, 2025-03-23:
Chip Thomas

Chipper2, 2025-03-23:
I will reprint.

Thank you so much for the customer service!!!
Chip Thomas

Chipper2, 2025-03-23:
I reprited the push art.  But its like the nub on the end of the motor is't long/big enough.  Am I suspose to print a different one?

Shaztech, 2025-03-25:
I've printed another tray for myself. And tested the Arm V2 (this arm was designed by another user) and it's not working... I will work on that and update the file. I will tell you when it's done.

Chipper2, 2025-03-25:
No problem.  I actually went back and printed the original that you did.  The one that has several parts seems to be working well.  thank you for letting me know.

Shaztech, 2025-03-25:
Yeah the original is reliable. I have 5 trays with it, and use it daily for the last year plus. No problem, more parts but reliable.

Chipper2, 2025-03-26:
I didn’t mean to get the V2 arm banned. lol

Is there a way to get the esp32 and touch scream separate?  I’m still having problems with my soldering.

Shaztech, 2025-03-26:
I've tried to fix the V2 arm (that I never tested before) for 5 hours, like 8 prints differents. And it wasn't working... 
I gave up, printed my original version, first try and it was working perfectly. I don't want people to have something that is not reliable in a pill dispenser that is crucial.

For the esp32 and touch screen, you can buy parts separate and find the schematic to connect everything at the same place on the esp. But it's just MORE (a lot more) soldering.

Just contact [jsondag](https://github.com/jsondag) is selling kits, you can email him at: [09-snakes.timbres@icloud.com](mailto:09-snakes.timbres@icloud.com). He will help you.

Shaztech, 2025-03-26:
Also if you mess some pads where the led was, you can find them directly on the ESP32, check a pinout of the module.

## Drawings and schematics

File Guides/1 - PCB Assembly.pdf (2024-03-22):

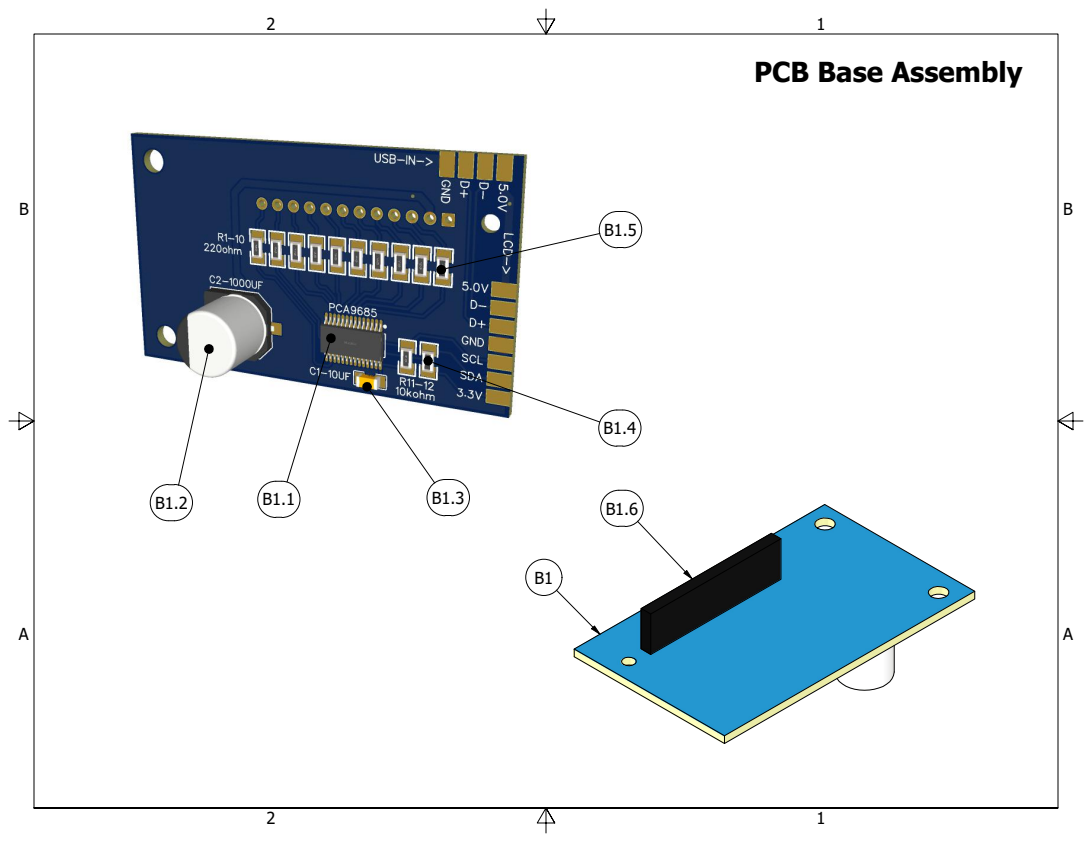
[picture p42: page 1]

PCB Base Assembly

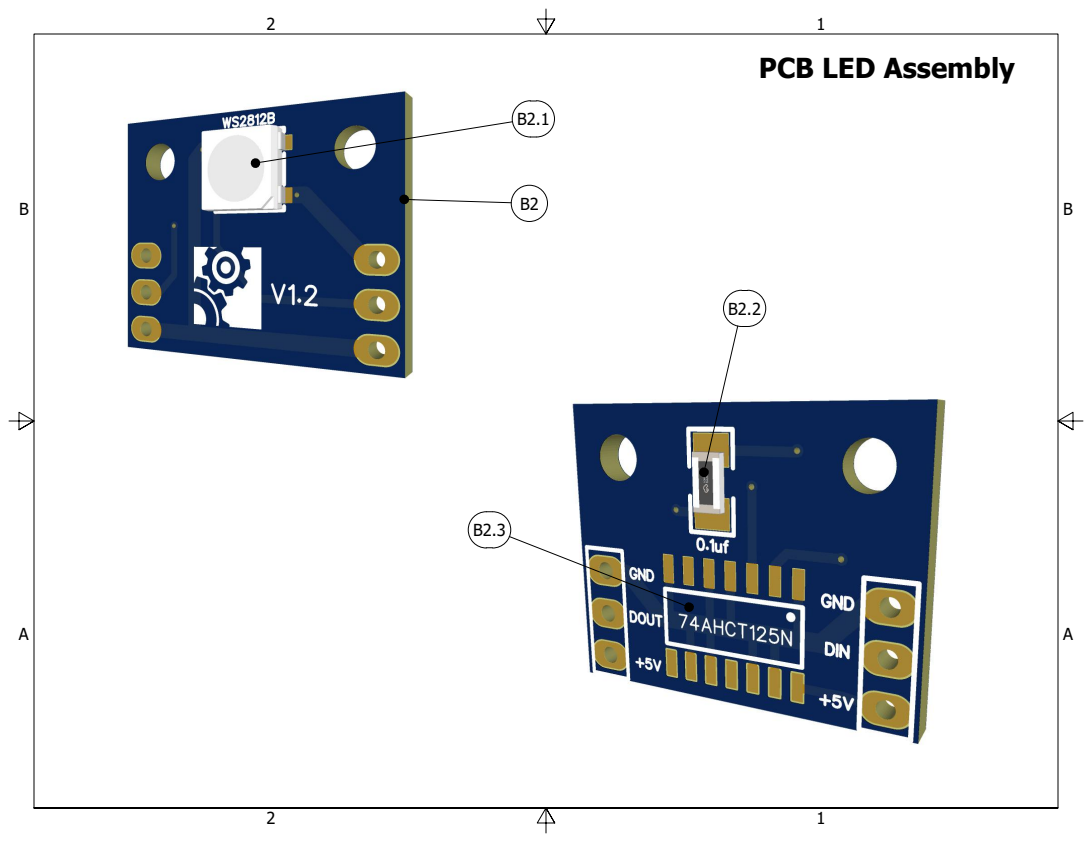
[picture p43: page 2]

PCB LED Assembly

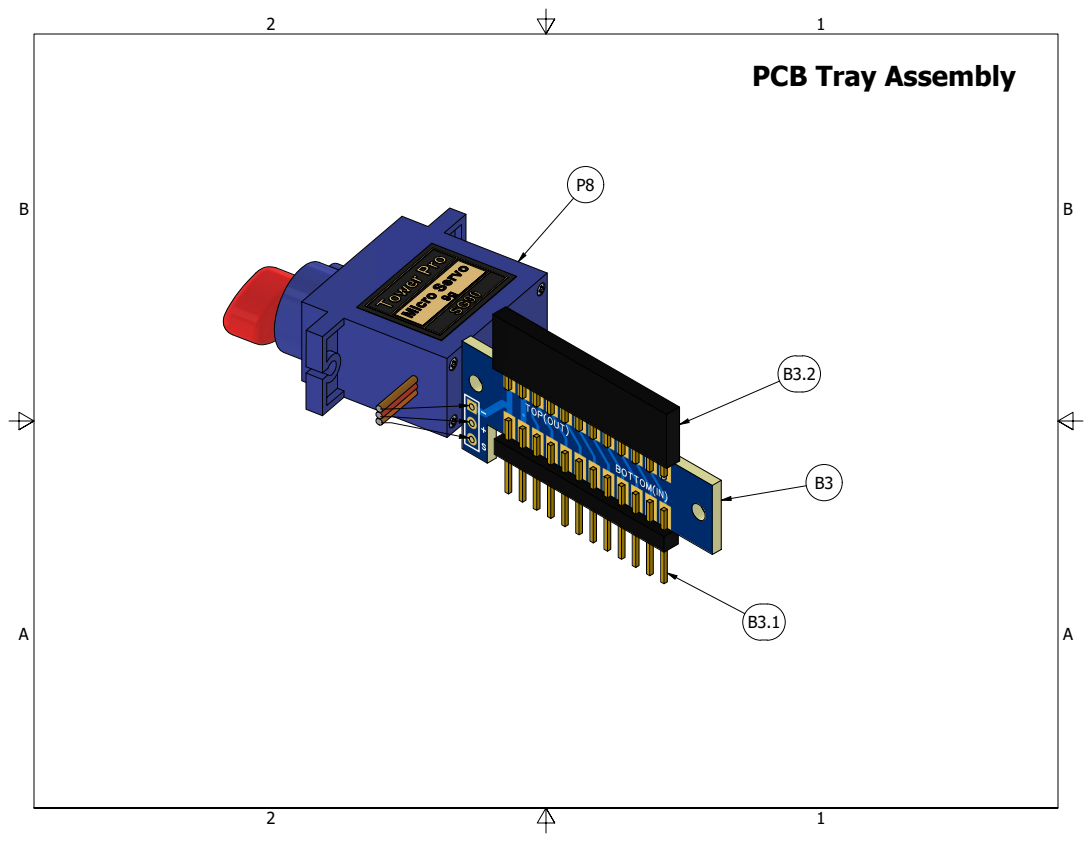
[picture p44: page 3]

PCB Tray Assembly

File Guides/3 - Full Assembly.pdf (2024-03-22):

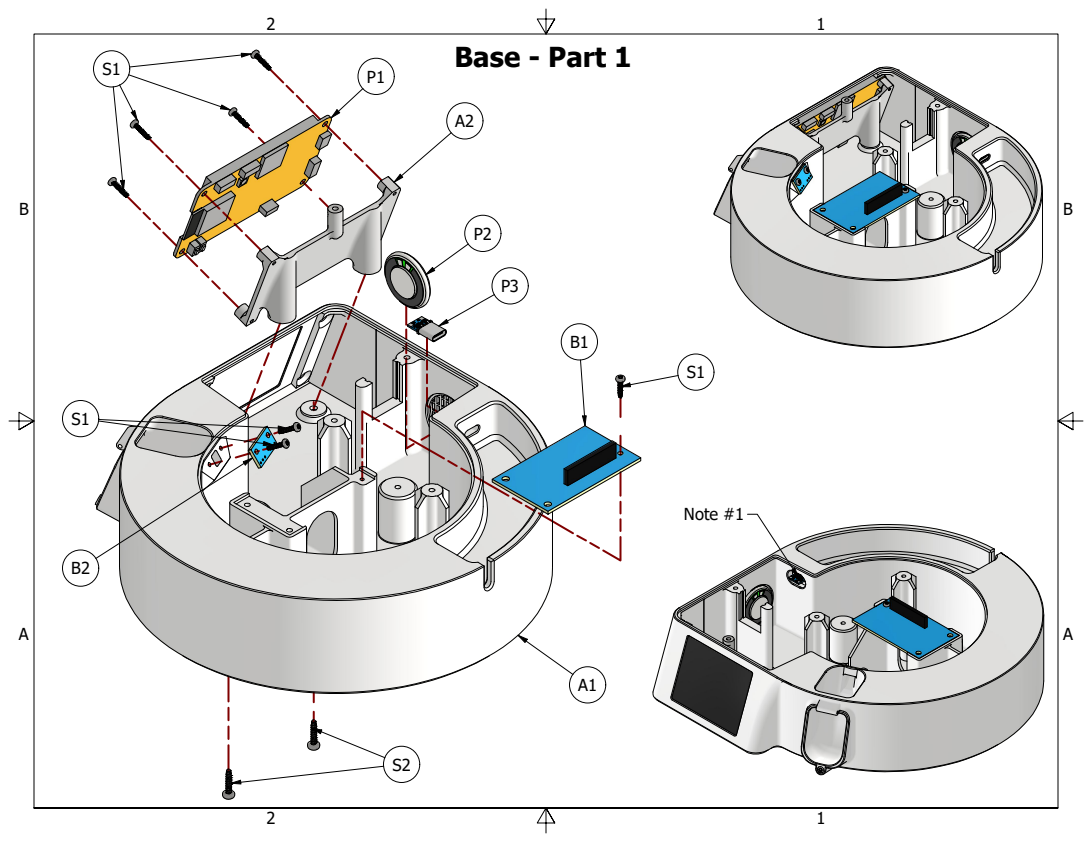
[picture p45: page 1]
Base - Part 1; Note #1

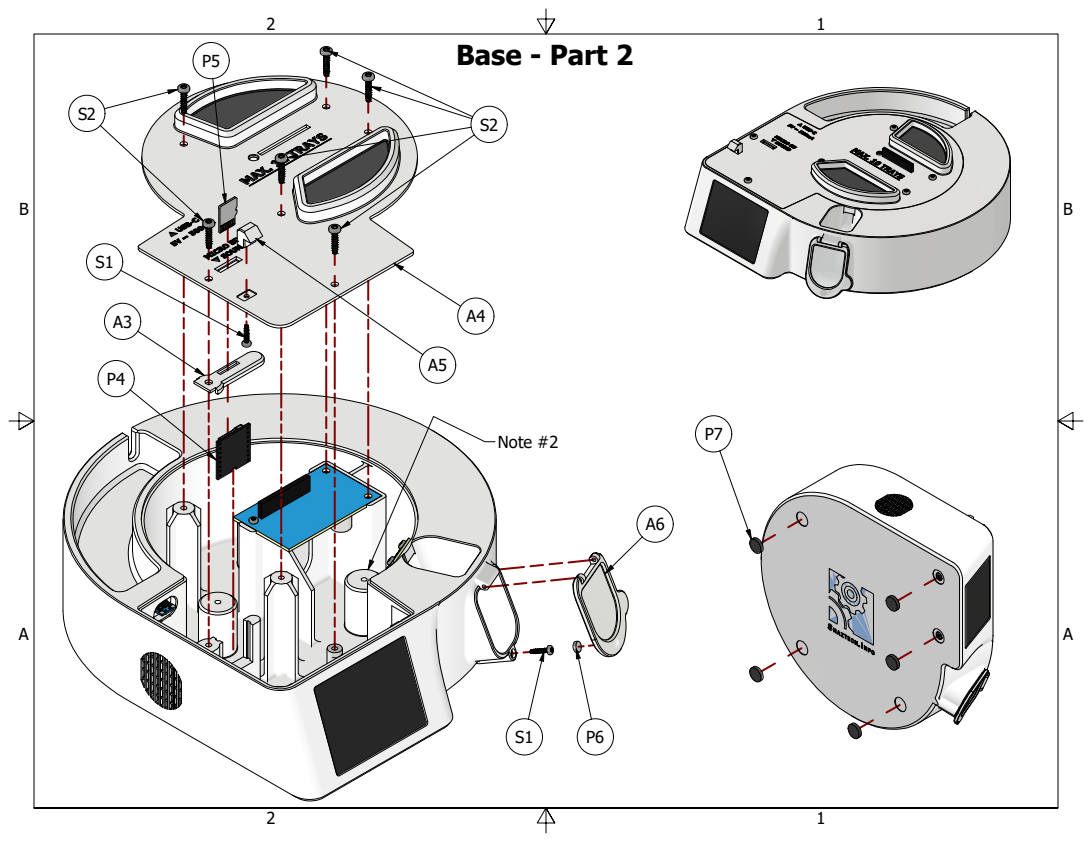
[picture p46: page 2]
Base - Part 2; P7 Note #2

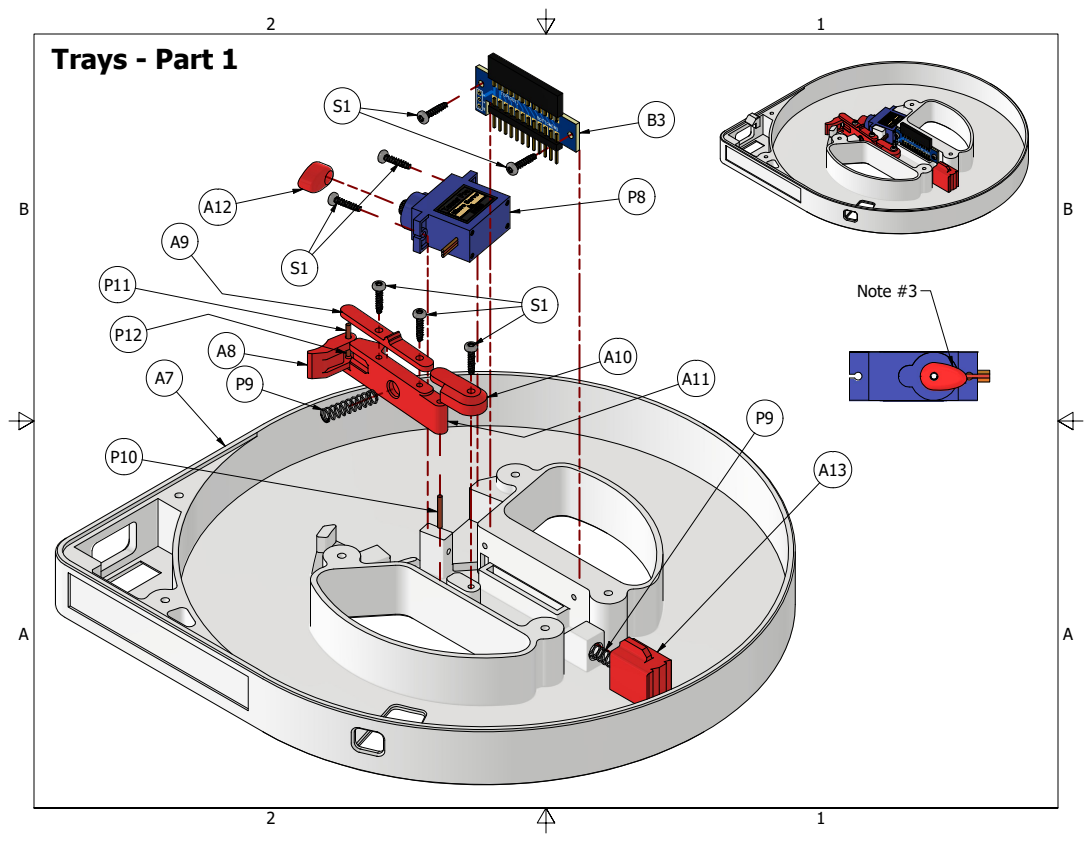
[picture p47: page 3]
Trays - Part 1; Note #3

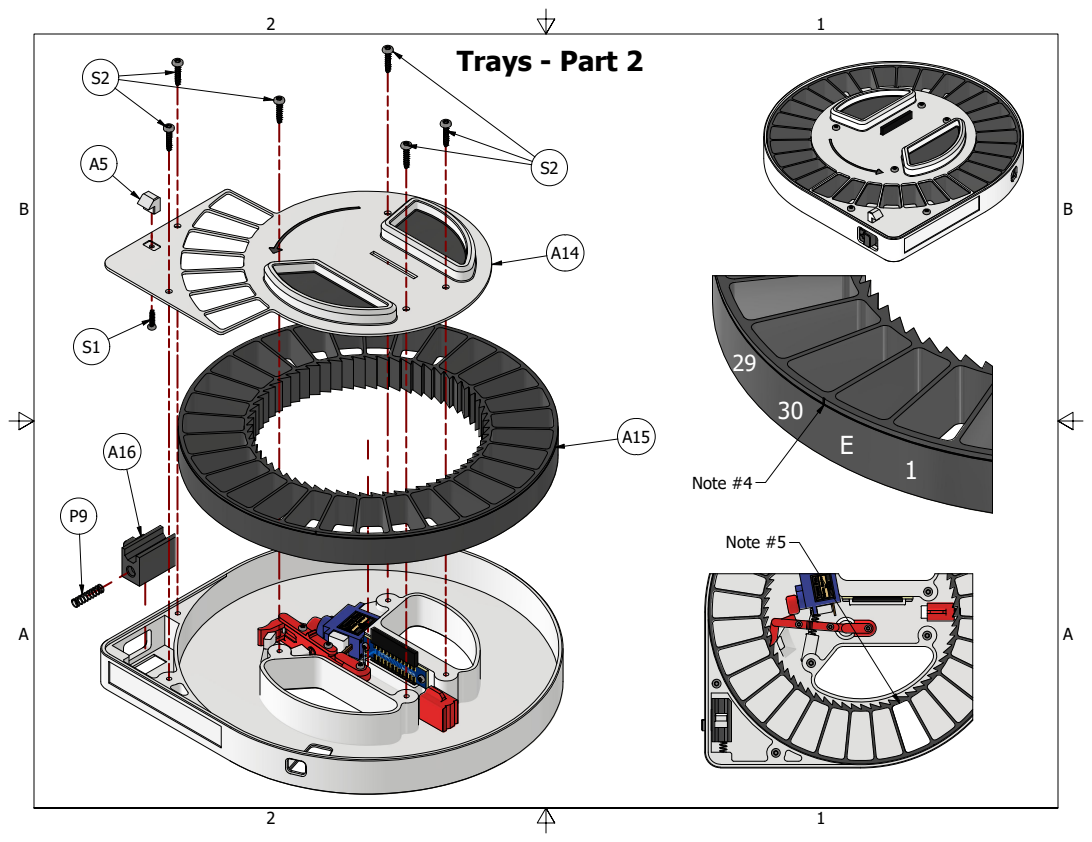
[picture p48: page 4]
Trays - Part 2; Note #4; Note #5

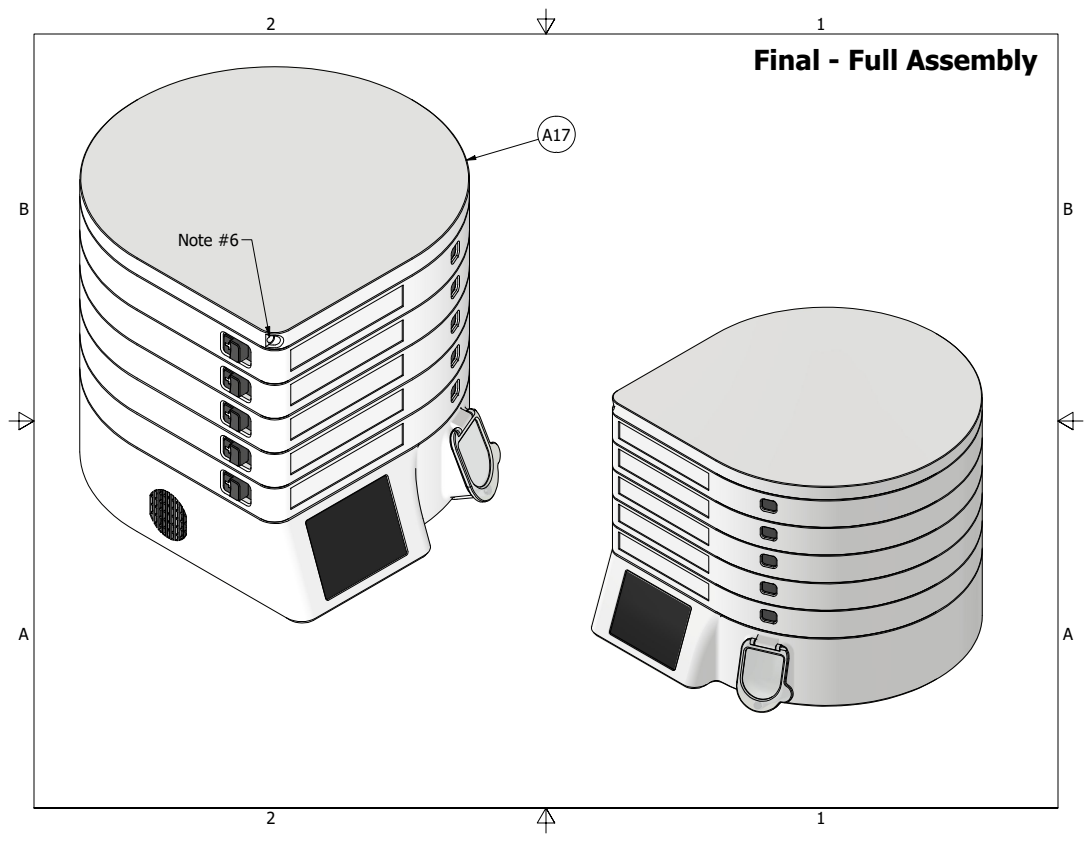
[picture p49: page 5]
Note #6

Final - Full Assembly

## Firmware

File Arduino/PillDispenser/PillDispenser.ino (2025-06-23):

/// ESP32 Dev Module
/// Minimal SPIFF

#include <lvgl.h>
#include <TFT_eSPI.h>
#include <ui.h>
#include <XPT2046_Touchscreen.h>
#include <WiFi.h>
#include <ESPmDNS.h>
#include <AsyncTCP.h>
#include <ESPAsyncWebServer.h>
#include <SPIFFS.h>
#include <AsyncElegantOTA.h>
#include <Preferences.h>
#include <Wire.h>
#include <Adafruit_PWMServoDriver.h>
#include "time.h"
#include <Adafruit_NeoPixel.h>
#include "DFRobotDFPlayerMini.h"
#include <WiFiClientSecure.h>
#include <UniversalTelegramBot.h>
#include <ArduinoJson.h>
#include "esp_task_wdt.h"

#define XPT2046_IRQ 36
#define XPT2046_MOSI 32
#define XPT2046_MISO 39
#define XPT2046_CLK 25
#define XPT2046_CS 33
#define SERVOMIN  150 // This is the 'minimum' pulse length count (out of 4096)
#define SERVOMAX  600 // This is the 'maximum' pulse length count (out of 4096)
#define SERVO_NUM 0
#define SDA_PIN 22
#define SCL_PIN 27
#define SAMPLE_RATE 16000 // Adjust based on your WAV file
#define DAC_CHANNEL 26 // GPIO 26
#define LED_PIN    16  // Use GPIO16
#define NUM_LEDS   2  // Number of LEDs in your strip

// declaration
String versionnumber = "v.1.9";
String HOSTNAME;
lv_timer_t* inactivity_timer = NULL;
lv_timer_t* alertsound_timer = NULL;
static const uint16_t screenWidth  = 320;
static const uint16_t screenHeight = 240;
static lv_disp_draw_buf_t draw_buf;
static lv_color_t buf[ screenWidth * screenHeight / 10 ];
uint16_t touchScreenMinimumX = 300, touchScreenMaximumX = 3800, touchScreenMinimumY = 220, touchScreenMaximumY = 3800;
String ssidload, passwordload;
bool systemloaded = false;
String trayNames[11] = {"", "", "", "", "", "", "", "", "", "", ""};
String BOT_TOKEN;
String CHAT_ID;
String passcode;
bool enabledpasscode = false;
int nextaction = 0;
int telegramalertinterval;
bool telegram_alertonce = false;
bool trayAlertEna[11] = {false, false, false, false, false, false, false, false, false, false, false};
bool traytriggered[11] = {false, false, false, false, false, false, false, false, false, false, false};
bool trayEnabled[11] = {false, false, false, false, false, false, false, false, false, false, false};
bool traydisptoday[11] = {false, false, false, false, false, false, false, false, false, false, false};
bool traydismtoday[11] = {false, false, false, false, false, false, false, false, false, false, false};
bool alreadyTriggered[11] = {false};
bool trayCheckedState[11] = {false}; // Initialize all as unchecked
bool trayfastflash[11];
bool solidLED;
bool fixaligment = false;
int trayHours[11];
int trayMin[11];
int resetHours;
int resetMin;
int trayColor[11];
bool alertinprogress = false;
bool dismissinprogress;
bool dispensebatchinprogress;
bool displacementinprogress;
int currentcolordispense;
int flashing;
uint32_t currentpixelcolor;
lv_obj_t* ui_TrayIMG[11];
lv_obj_t* ui_TrayLBL[11];
lv_obj_t* ui_TrayCheckIMG[11];

bool internetstatus;
bool clockSS;
bool muteSound;
bool currentlyplaying;
int installedTrays;
bool dstEnabled;
int utcOffset;
int traytodispense;
int displacesteps;
int selectedtray;
int spkvolume;
int alertinterval;

const int buttonPin = 4;  // GPIO4
const int debounceDelay = 50;  // 50 milliseconds for debounce
unsigned long lastDebounceTime = 0;  // Time when the button was last toggled
int lastButtonState = HIGH;  // Previous state of the button
int buttonState = HIGH;  // Current reading from the button pin

// register stuff
SPIClass mySpi = SPIClass(VSPI);
AsyncWebServer server(80);
Preferences preferences;
XPT2046_Touchscreen ts(XPT2046_CS, XPT2046_IRQ);
TFT_eSPI tft = TFT_eSPI(screenWidth, screenHeight);
Adafruit_PWMServoDriver pwm = Adafruit_PWMServoDriver();
Adafruit_NeoPixel pixels = Adafruit_NeoPixel(NUM_LEDS, LED_PIN, NEO_GRB + NEO_KHZ800);
DFRobotDFPlayerMini myDFPlayer;
WiFiClientSecure secured_client;
UniversalTelegramBot* bot = nullptr;


void setup() {
  Serial.begin( 115200 );
  Serial2.begin(9600, SERIAL_8N1, -1, 17);
  esp_task_wdt_init(15, true);
  pinMode(4, INPUT_PULLUP);

  if (!SPIFFS.begin()) {
    return;
  }

  String showversion = "LVGL v";
  showversion += String('.') + lv_version_major() + "." + lv_version_minor() + "." + lv_version_patch();
  showversion += " - SOFT " + versionnumber; // SOFTWARE VERSION DEFINITION

  Wire.begin(SDA_PIN, SCL_PIN);
  pwm.begin();
  pwm.setPWMFreq(60);

  myDFPlayer.begin(Serial2);
  myDFPlayer.volume(1);  //Set volume value. From 0 to 30

  pixels.begin();

  /*Initialize the display*/
  lv_init();
#if LV_USE_LOG != 0
  lv_log_register_print_cb( my_print ); /* register print function for debugging */
#endif
  mySpi.begin(XPT2046_CLK, XPT2046_MISO, XPT2046_MOSI, XPT2046_CS);
  ts.begin(mySpi);
  ts.setRotation(3);
  tft.begin();
  tft.setRotation(3);
  lv_disp_draw_buf_init( &draw_buf, buf, NULL, screenWidth * screenHeight / 10 );
  static lv_disp_drv_t disp_drv;
  lv_disp_drv_init( &disp_drv );
  disp_drv.hor_res = screenWidth;
  disp_drv.ver_res = screenHeight;
  disp_drv.flush_cb = my_disp_flush;
  disp_drv.draw_buf = &draw_buf;
  lv_disp_drv_register( &disp_drv );
  static lv_indev_drv_t indev_drv;
  lv_indev_drv_init( &indev_drv );
  indev_drv.type = LV_INDEV_TYPE_POINTER;
  indev_drv.read_cb = my_touchpad_read;
  lv_indev_t * my_indev = lv_indev_drv_register( &indev_drv );

  ui_init(); //// BEFORE ANYTHING RELATED TO LVGL !!!!!

  ui_TrayIMG[1] = ui_TrayIMG1;
  ui_TrayIMG[2] = ui_TrayIMG2;
  ui_TrayIMG[3] = ui_TrayIMG3;
  ui_TrayIMG[4] = ui_TrayIMG4;
  ui_TrayIMG[5] = ui_TrayIMG5;
  ui_TrayIMG[6] = ui_TrayIMG6;
  ui_TrayIMG[7] = ui_TrayIMG7;
  ui_TrayIMG[8] = ui_TrayIMG8;
  ui_TrayIMG[9] = ui_TrayIMG9;
  ui_TrayIMG[10] = ui_TrayIMG10;

  ui_TrayLBL[1] = ui_TrayLBL1;
  ui_TrayLBL[2] = ui_TrayLBL2;
  ui_TrayLBL[3] = ui_TrayLBL3;
  ui_TrayLBL[4] = ui_TrayLBL4;
  ui_TrayLBL[5] = ui_TrayLBL5;
  ui_TrayLBL[6] = ui_TrayLBL6;
  ui_TrayLBL[7] = ui_TrayLBL7;
  ui_TrayLBL[8] = ui_TrayLBL8;
  ui_TrayLBL[9] = ui_TrayLBL9;
  ui_TrayLBL[10] = ui_TrayLBL10;

  ui_TrayCheckIMG[1] = ui_TrayCheckIMG1;
  ui_TrayCheckIMG[2] = ui_TrayCheckIMG2;
  ui_TrayCheckIMG[3] = ui_TrayCheckIMG3;
  ui_TrayCheckIMG[4] = ui_TrayCheckIMG4;
  ui_TrayCheckIMG[5] = ui_TrayCheckIMG5;
  ui_TrayCheckIMG[6] = ui_TrayCheckIMG6;
  ui_TrayCheckIMG[7] = ui_TrayCheckIMG7;
  ui_TrayCheckIMG[8] = ui_TrayCheckIMG8;
  ui_TrayCheckIMG[9] = ui_TrayCheckIMG9;
  ui_TrayCheckIMG[10] = ui_TrayCheckIMG10;

  lv_obj_add_event_cb(ui_ScanWifiBTN, scan_wifi_event_handler, LV_EVENT_ALL, NULL);
  lv_obj_add_event_cb(ui_Keyboard, keyboard_wifi_event_handler, LV_EVENT_ALL, NULL);
  lv_obj_add_event_cb(ui_PassKey, passkey_event_handler, LV_EVENT_ALL, NULL);
  lv_obj_add_event_cb(ui_SettingBackBTN, SettingBackBTN_event_handler, LV_EVENT_ALL, NULL);
  lv_obj_add_event_cb(ui_SettingBTN, SettingBTN_event_handler, LV_EVENT_ALL, NULL);
  lv_obj_add_event_cb(ui_WifiClearBTN, WifiClearBTN_event_handler, LV_EVENT_ALL, NULL);
  lv_obj_add_event_cb(ui_DispenseBTN, DispenseBTN_event_handler, LV_EVENT_ALL, NULL);
  lv_obj_add_event_cb(ui_TrueDismissBTN, TrueDismissBTN_event_handler, LV_EVENT_ALL, NULL);
  lv_obj_add_event_cb(ui_DispenseAgainBTN, DispenseAgainBTN_event_handler, LV_EVENT_ALL, NULL);
  lv_obj_add_event_cb(ui_DoubleDispenseCancelBTN, DoubleDispenseCancelBTN_event_handler, LV_EVENT_ALL, NULL);
  lv_obj_add_event_cb(ui_LCDLBL, LCDLBL_event_handler, LV_EVENT_ALL, NULL);

  lv_obj_add_event_cb(ui_UpIMGBTN, UpIMGBTN_event_handler, LV_EVENT_ALL, NULL);
  lv_obj_add_event_cb(ui_DownIMGBTN, DownIMGBTN_event_handler, LV_EVENT_ALL, NULL);
  lv_obj_add_event_cb(ui_TraycfgBTN, TraycfgBTN_event_handler, LV_EVENT_ALL, NULL);
  lv_obj_add_event_cb(ui_TrayCfgSaveBTN, TrayCfgSaveBTN_event_handler, LV_EVENT_ALL, NULL);
  lv_obj_add_event_cb(ui_TrayCfgClearBTN, TrayCfgClearBTN_event_handler, LV_EVENT_ALL, NULL);
  lv_obj_add_event_cb(ui_VolTestBTN, VolTestBTN_event_handler, LV_EVENT_ALL, NULL);
  lv_obj_add_event_cb(ui_DisplaceBTN, DisplaceBTN_event_handler, LV_EVENT_ALL, NULL);
  lv_obj_add_event_cb(ui_HalfDisplaceBTN, HalfDisplaceBTN_event_handler, LV_EVENT_ALL, NULL);
  lv_obj_add_event_cb(ui_ColorRoller, roller_event_handler, LV_EVENT_VALUE_CHANGED, NULL);
  lv_obj_add_event_cb(ui_PickPillsSCR, pick_pills_screen_event_handler, LV_EVENT_CLICKED, NULL);

  for (int i = 1; i <= 10; i++) {
    lv_obj_add_event_cb(ui_TrayIMG[i], tray_check_event_handler, LV_EVENT_ALL, NULL);
  }

  lv_obj_add_state(ui_Keyboard, LV_STATE_DISABLED);
  lv_obj_add_state(ui_PassTxtBox, LV_STATE_DISABLED);
  lv_obj_add_flag(ui_WifiScanPAN, LV_OBJ_FLAG_HIDDEN);

  lv_label_set_text(ui_VersionLBL, showversion.c_str());

  lv_timer_t* timer = lv_timer_create(startup_step1_timer, 1000, NULL);
  pixels.setPixelColor(0, pixels.Color(213, 230, 255));
  pixels.setPixelColor(1, pixels.Color(213, 230, 255));
  pixels.setBrightness(50);
  pixels.show();
  loadSettings();
}


void loop()
{
  int reading = digitalRead(buttonPin);

  if (reading != lastButtonState) {
    lastDebounceTime = millis();  // Reset the debouncing timer
  }

  if ((millis() - lastDebounceTime) > debounceDelay) {
    if (reading != buttonState) {
      buttonState = reading;

      if (buttonState == LOW) {
        Serial.println("Physical Dispense Button Pressed");

        if (alertinprogress) { // Alert dispense (1 tray or more)
          for (int i = 1; i <= 10; i++) {
            if (i == 10) {
              alertinprogress = false;
            }
            if (traytriggered[i]) {
              dispensebatchinprogress = true;
              currentpixelcolor = index_to_pixel(trayColor[i]);
              currentcolordispense = trayColor[i];
              dispensebatch(currentcolordispense);
              break;
            }
            lv_obj_add_state(ui_DispenseBTN, LV_STATE_DISABLED); // Disable the button
            lv_obj_add_state(ui_TraycfgBTN, LV_STATE_DISABLED); // Disable the button
          }
        }
      }
    }
  }

  lastButtonState = reading;  // Save the current state

  lv_timer_handler(); /* let the GUI do its work */
  lv_task_handler();

}

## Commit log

2024-03-22 first upload
    [A1 - Base Bottom [1x].stl, A1.1 - Base Washer Holder [3x OPT].stl, A10 - Arm Lock [1x per Tray].stl, A11 - Arm [1x per Tray].stl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]
2024-03-25 Rename A1 - Base Bottom - Model with cup [1x].stl to A1b - Base Bottom - Model with cup [1x].stl
    [A1b - Base Bottom - Model with cup [1x].stl]
2024-03-25 Rename A1 - Base Bottom [1x].stl to A1 - Base Bottom - Model with door [1x].stl
    [A1 - Base Bottom - Model with door [1x].stl, A1 - Base Bottom [1x].stl]
2024-03-26 Update README.md
    added voltages to the capacitors
2024-03-29 Add files via upload
    Fixed a gap
    [A17 - Top Dust Cap [1x].stl]
2024-04-02 Fix Speaker Grill
    [A1 - Base Bottom - Model with door [1x].stl, A1b - Base Bottom - Model with cup [1x].stl]
2024-04-05 Update A11 - Arm [1x per Tray].stl
    Added notch for taller servos
    [A11 - Arm [1x per Tray].stl]
2024-04-06 Adjusted posts for larger washers
    [A1 - Base Bottom - Model with door [1x].stl, A1b - Base Bottom - Model with cup [1x].stl]
2024-10-11 Delete 3D Printed Parts STL directory
    Go to
    https://makerworld.com/en/models/389626
    for the models
    [A1 - Base Bottom - Model with door [1x].stl, A1.1 - Base Washer Holder [3x OPT].stl, A1.2 - Base Cup [1x OPT].stl, A10 - Arm Lock [1x per Tray].stl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]
2024-12-21 Update 2 - Wiring.pdf
2025-11-10 Add files via upload
    Here's a BOM list for LCSC, thanks to @interlock (https://github.com/interlock)
    [LCSC BOM List.csv]
